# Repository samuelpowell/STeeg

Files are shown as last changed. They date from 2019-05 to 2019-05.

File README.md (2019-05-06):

# STeeg

# Startup
  - tPOR = 2^18 x tclk
  - tRST = 2 x tclk

# Form factor

 - To fit Takachi HEN110512 (S/B) external W111.2 x H54.7 x D120mm, internal 99.2W x H49.7 x D116mm.

# Configuration

  - Referential montage using SRB1 internally routed negative inputs.
  - Internal BIAS amplifier is used to reject interference and set patien common mode, components are chosen in bias amplifier feedback path to attain sufficient bandiwdth.
  - RC network on input is a low pass filter with differential capacitor to VREF, assuming fclk = 2.048MHz, the first alias is at fMOD = 1.024MHz and this should have good attenuation.

# Layout, power and passives.

  - AVDD and AVDD1 must be quiet. AVDD1 is the charge pump supply which may have switch transients. AVDD1 and AVSS1 should be starred, and each supply should be bypassed with 10u and 0.1u solid ceramic capacitors.
  - VCAP1 can be MLCC but for improved performance under vibration a tantalum or class 1 (C0G/NPO) should be used.
  - At output, provide VREF and VBIAS for differential capacitance and bias bpins
  - Decoupling capacitors and VCAP1 - VCAP4 should be as close as possible.
  - Optionally split analogue and digital planes, route over the appropriate plane
  - Use COG for differentials
  - 

# Architecture
 - 6-XV quiet input, isolated
 - 
# Component choices

 - Analogue LDO (TPS717 selected)
  - EVM uses TPS73225 on bipolar, 30uV (10-100kHz), 1% accuracy, 37dB @ 10kHz, 58dB @ 100Hz
  - TPS793 200mA, 70dB @ 10kHz, 112mv dropout, SOT-23
  - TPS77350, 55dB @ 1kHz, 30uV
  - TPS717XX, 70dB @ 1kHz, 67dB @100kHz, 30uV (100Hz - 100kHz), SOT-23

# Chaining multiple channels

# Notes

  - ADD LEDs
  - ADD Test Points
 - MICROCONTROLLER BOOT
 - MCU PROG
 - optional 3.3v external

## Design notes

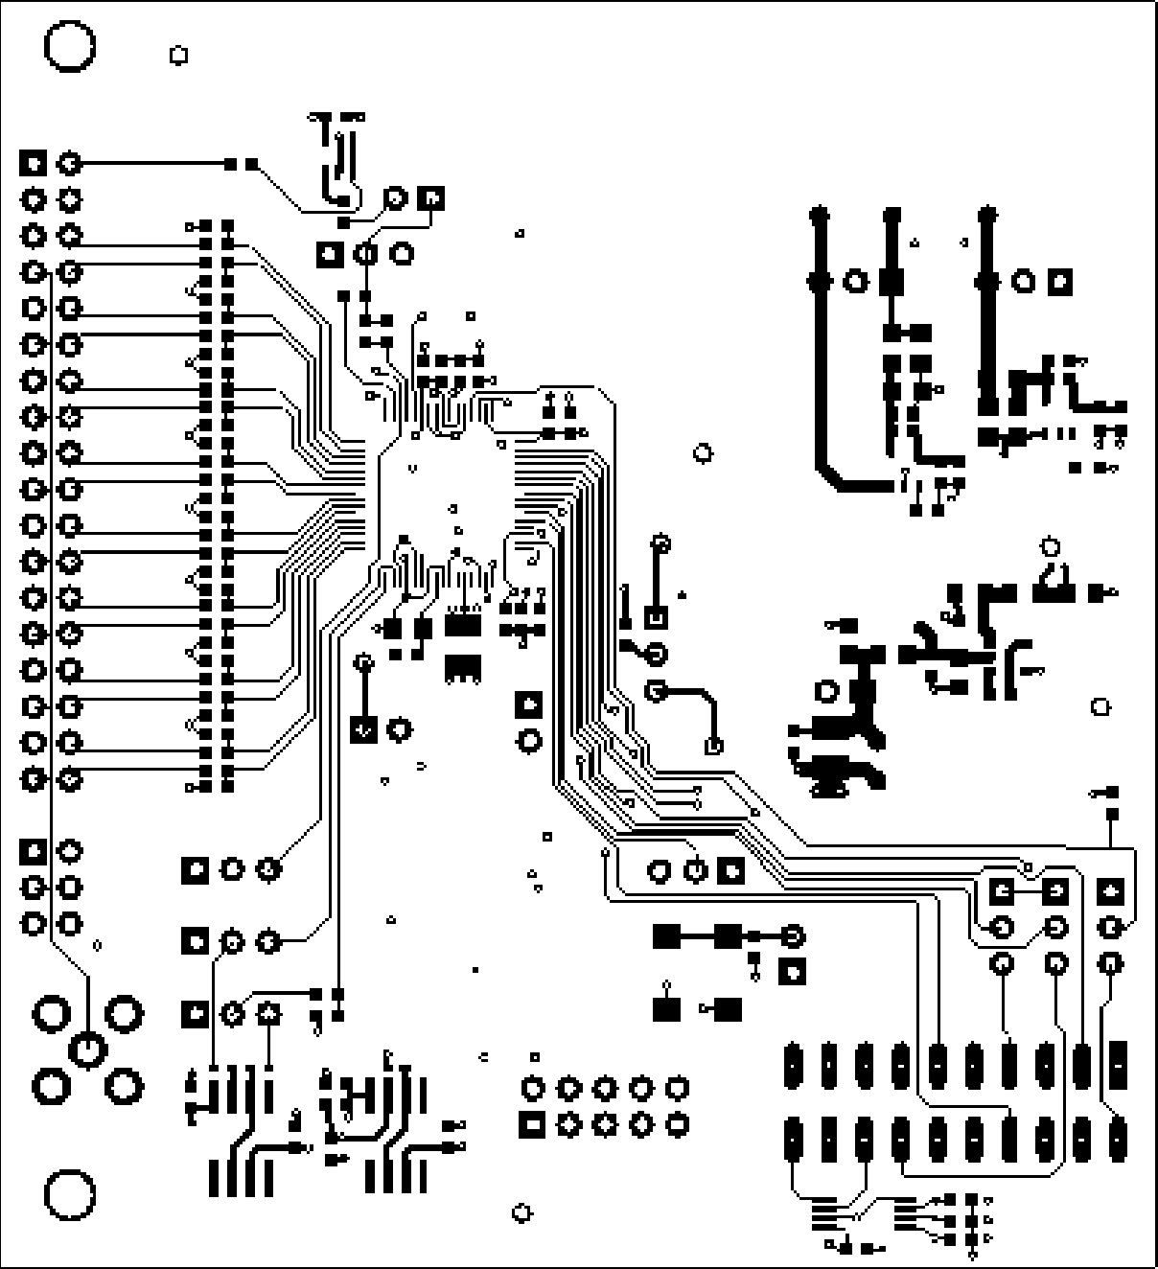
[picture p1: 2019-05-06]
evm_top.png

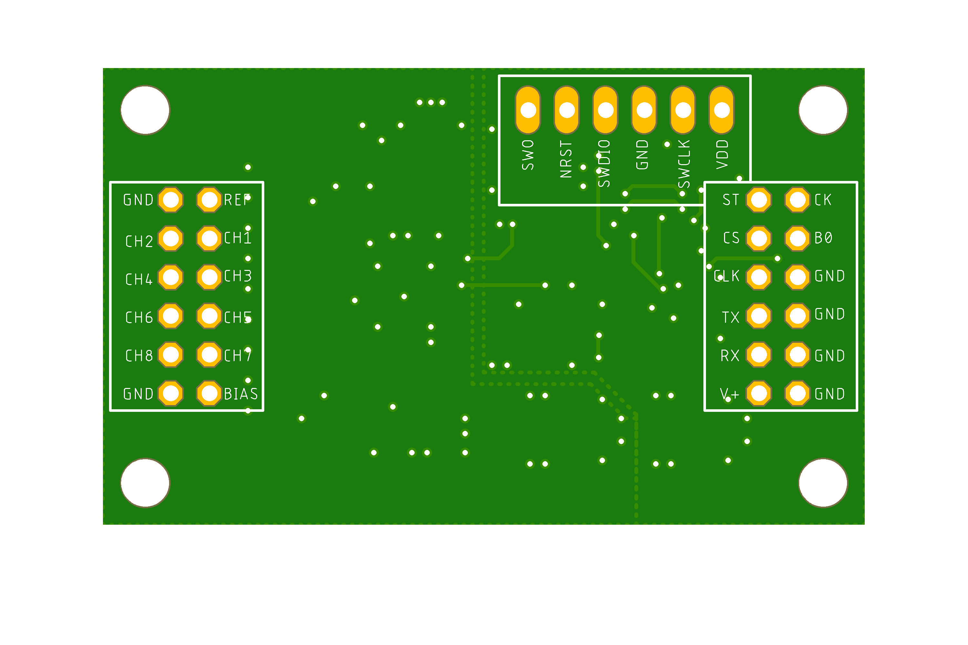
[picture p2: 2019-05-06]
stEEG/REV_A/stEEG_bottom.png

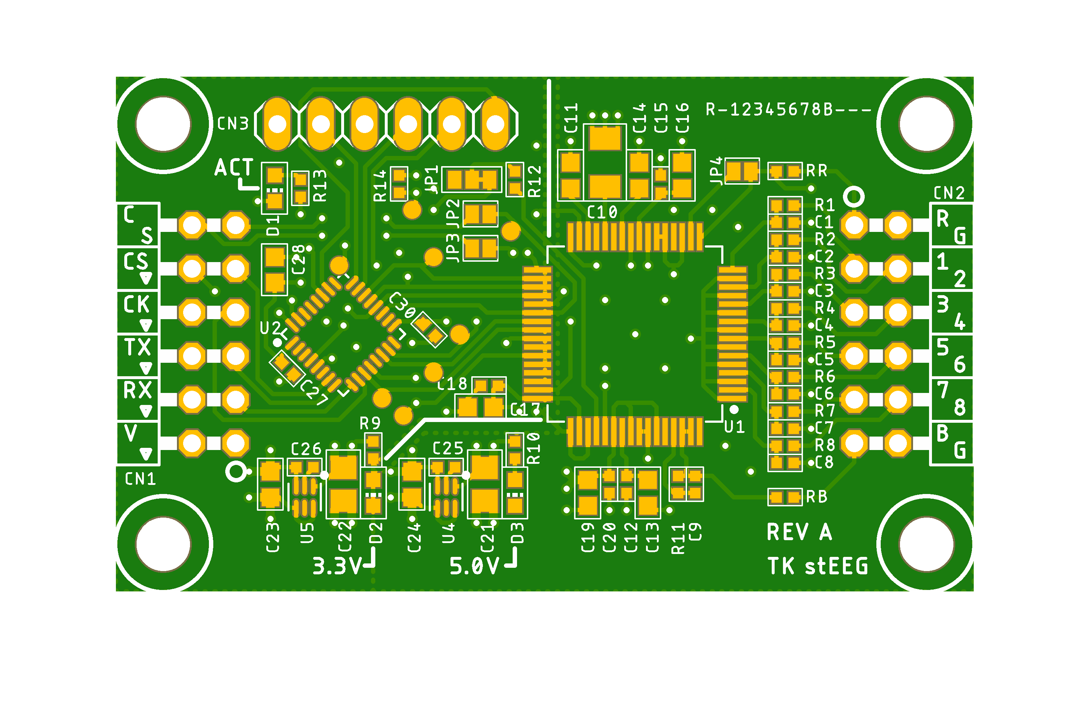
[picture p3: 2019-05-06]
stEEG/REV_A/stEEG_top.png

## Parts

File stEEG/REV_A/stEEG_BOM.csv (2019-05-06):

Parts | Qty | Value | Tolerance | Manufacturer | Part No | Digikiey | Package | Description
D1, D2, D3 | 3 |  |  | OSRAM Opto Semiconductors Inc. | LB Q39G-L2OO-35-1 | 475-2816-6-ND | 0603 | LED
CN3 | 1 |  |  | Molex | 901200126 | WM8076-ND |  | Pin header straight
CN1, CN2 | 2 |  |  | Molex | 10-88-3121 | WM23740-ND |  | Pin header 90 deg
R12, R14 | 2 | 100k | 1%, 0.0625W, 50V, 400ppm | Generic |  |  | 0402 | Resistor
C13, C15, C18, C20, C27, C30 | 6 | 100n | 10%, X7R, 16V | Generic |  |  | 0402 | Capacitor
C10 | 1 | 100u | 10%, X5R, 6.3V | Murata | GRM31CR60J107KE39L | 490-13982-1-ND | 1206 | Capacitor
C16, C28 | 2 | 10u | 10%, X5R, 16V | Murata | GRM188R61C106KAALD | 490-10728-1-ND | 0603 | Capacitor
C21, C22 | 2 | 10u | 10%, X7S, 16V | Murata | GRM21BC71C106KE11L | 490-12756-1-ND | 0805 | Capacitor
R9, R13 | 2 | 150R | 1%, 0.0625W, 50V, 400ppm | Generic |  |  | 0402 | Resistor
R11 | 1 | 1M | 1%, 0.0625W, 50V, 400ppm | Generic |  |  | 0402 | Resistor
R10 | 1 | 1k | 1%, 0.0625W, 50V, 400ppm | Generic |  |  | 0402 | Resistor
C9 | 1 | 1n5 | 10%, X7R, 50V | Generic |  |  | 0402 | Capacitor
C11, C12, C14, C17, C19, C23, C24 | 7 | 1u | 10%, X7R, 16V | Generic |  |  | 0603 | Capacitor
C25, C26 | 2 | 22n | 10%, X7R, 50V | Generic |  |  | 0402 | Capacitor
R1, R2, R3, R4, R5, R6, R7, R8, RB, RR | 10 | 4k99 | 1%, 0.0625W, 50V, 400ppm | Generic |  |  | 0402 | Resistor
C1, C2, C3, C4, C5, C6, C7, C8 | 8 | 4n7 | 10%, X7R, 50V | Generic |  |  | 0402 | Capacitor
U1 | 1 |  |  | Texas Instruments | ADS1299IPAG | 296-35009-ND | TQFP64 | 8-Channel, 24-Bit Analog-To-Digital Converter With Integrated EEG Front End
U2 | 1 |  |  | ST Microelectronics | STM32L432KCU3 | 497-18596-ND | QFN32 | Low-power ARM M4 microcontroller
U5 | 1 |  |  | Texas Instruments | TPS71733DSE | 296-32543-1-ND | SON8 | Low-Noise, High-Bandwidth PSRR, Low-Dropout, 150-mA Linear Regulator
U4 | 1 |  |  | Texas Instruments | TPS71750DSE | 296-25447-1-ND | SON8 | Low-Noise, High-Bandwidth PSRR, Low-Dropout, 150-mA Linear Regulator

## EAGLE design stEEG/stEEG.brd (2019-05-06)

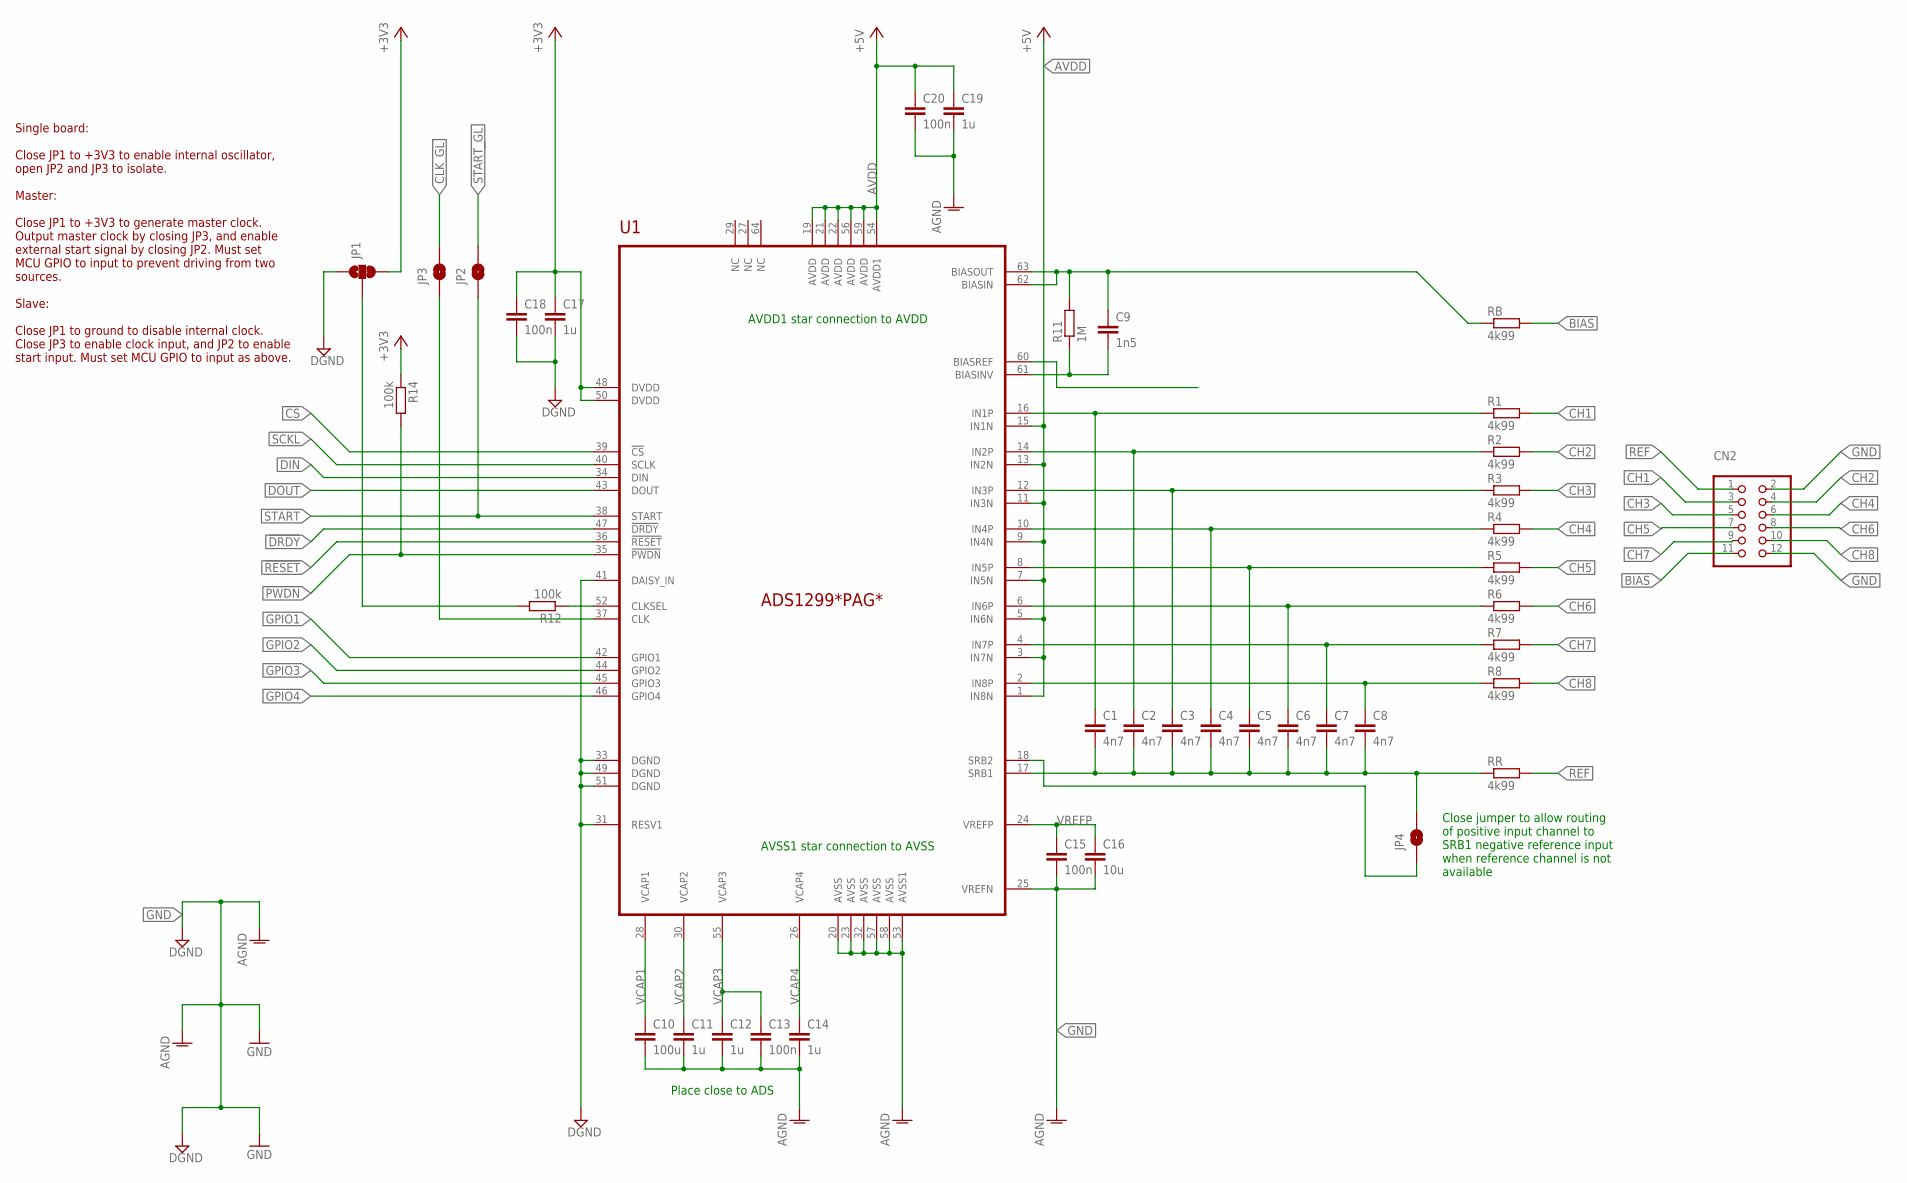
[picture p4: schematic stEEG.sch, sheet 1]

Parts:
C1, C2, C3, C4, C5, C6, C7, C8: 4n7; C0402
C9: 1n5; C0402
C10: 100u; C1206
C11, C12, C14, C17, C19: 1u; C0603
C13, C15, C18, C20: 100n; C0402
C16: 10u; C0603
CN2: PINHD-2X6/90; 2X06/90
JP1: JUMPER-SMT_3_1-NC_TRACE_SILK; SMT-JUMPER_3_1-NC_TRACE_SILK
JP2, JP3, JP4: JUMPER-SMT_2_NO_SILK; SMT-JUMPER_2_NO_SILK
R1, R2, R3, R4, R5, R6, R7, R8: 4k99; R0402
R11: 1M; R0402
R12, R14: 100k; R0402
RB: 4k99; R0402
RR: 4k99; R0402
U1: ADS1299*PAG*; PAG-PQFP64

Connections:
!CS: U1.39 (!CS); also elsewhere on the board
!DRDY: U1.47 (!DRDY); also elsewhere on the board
!PWDN: R14.2, U1.35 (!PWDN); also elsewhere on the board
!RESET: U1.36 (!RESET); also elsewhere on the board
+3V3: C17.1, C18.1, JP1.3, R14.1, U1.48 (DVDD), U1.50 (DVDD); also elsewhere on the board
AVDD: C19.1, C20.1, U1.1 (IN8N), U1.3 (IN7N), U1.5 (IN6N), U1.7 (IN5N), U1.9 (IN4N), U1.11 (IN3N), U1.13 (IN2N), U1.15 (IN1N), U1.19 (AVDD), U1.21 (AVDD), U1.22 (AVDD), U1.54 (AVDD1), U1.56 (AVDD), U1.59 (AVDD); also elsewhere on the board
BIAS: CN2.11, RB.2
CH1: CN2.3, R1.2
CH2: CN2.4, R2.2
CH3: CN2.5, R3.2
CH4: CN2.6, R4.2
CH5: CN2.7, R5.2
CH6: CN2.8, R6.2
CH7: CN2.9, R7.2
CH8: CN2.10, R8.2
CLK_GL: JP3.2; also elsewhere on the board
DIN: U1.34 (DIN); also elsewhere on the board
DOUT: U1.43 (DOUT); also elsewhere on the board
GND: C10.2, C11.2, C12.2, C13.2, C14.2, C15.2, C16.2, C17.2, C18.2, C19.2, C20.2, CN2.2, CN2.12, JP1.1, U1.20 (AVSS), U1.23 (AVSS), U1.25 (VREFN), U1.31 (RESV1), U1.32 (AVSS), U1.33 (DGND), U1.41 (DAISY_IN), U1.49 (DGND), U1.51 (DGND), U1.53 (AVSS1), U1.57 (AVSS), U1.58 (AVSS); also elsewhere on the board
GPIO1: U1.42 (GPIO1)
GPIO2: U1.44 (GPIO2)
GPIO3: U1.45 (GPIO3)
GPIO4: U1.46 (GPIO4)
unnamed: C1.1, R1.1, U1.16 (IN1P)
unnamed: R12.1, U1.52 (CLKSEL)
unnamed: C3.1, R3.1, U1.12 (IN3P)
unnamed: C4.1, R4.1, U1.10 (IN4P)
unnamed: C9.2, R11.1, U1.61 (BIASINV)
unnamed: C6.1, R6.1, U1.6 (IN6P)
unnamed: C7.1, R7.1, U1.4 (IN7P)
unnamed: C9.1, R11.2, RB.1, U1.62 (BIASIN), U1.63 (BIASOUT)
unnamed: C2.1, R2.1, U1.14 (IN2P)
unnamed: C5.1, R5.1, U1.8 (IN5P)
unnamed: C8.1, R8.1, U1.2 (IN8P)
unnamed: JP4.1, U1.18 (SRB2)
unnamed: JP1.2, R12.2
unnamed: JP3.1, U1.37 (CLK)
REF: CN2.1, RR.2
SCKL: U1.40 (SCLK); also elsewhere on the board
START: JP2.1, U1.38 (START); also elsewhere on the board
START_GL: JP2.2; also elsewhere on the board
VCAP1: C10.1, U1.28 (VCAP1)
VCAP2: C11.1, U1.30 (VCAP2)
VCAP3: C12.1, C13.1, U1.55 (VCAP3)
VCAP4: C14.1, U1.26 (VCAP4)
VREFP: C15.1, C16.1, U1.24 (VREFP)
VREFX: C1.2, C2.2, C3.2, C4.2, C5.2, C6.2, C7.2, C8.2, JP4.2, RR.1, U1.17 (SRB1)

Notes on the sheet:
AVDD1 star connection to AVDD
AVSS1 star connection to AVSS
Place close to ADS
Close jumper to allow routing of positive input channel to SRB1 negative reference input when reference channel is not available
Single board: Close JP1 to +3V3 to enable internal oscillator, open JP2 and JP3 to isolate. Master: Close JP1 to +3V3 to generate master clock. Output master clock by closing JP3, and enable external start signal by closing JP2. Must set MCU GPIO to input to prevent driving from two sources. Slave: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

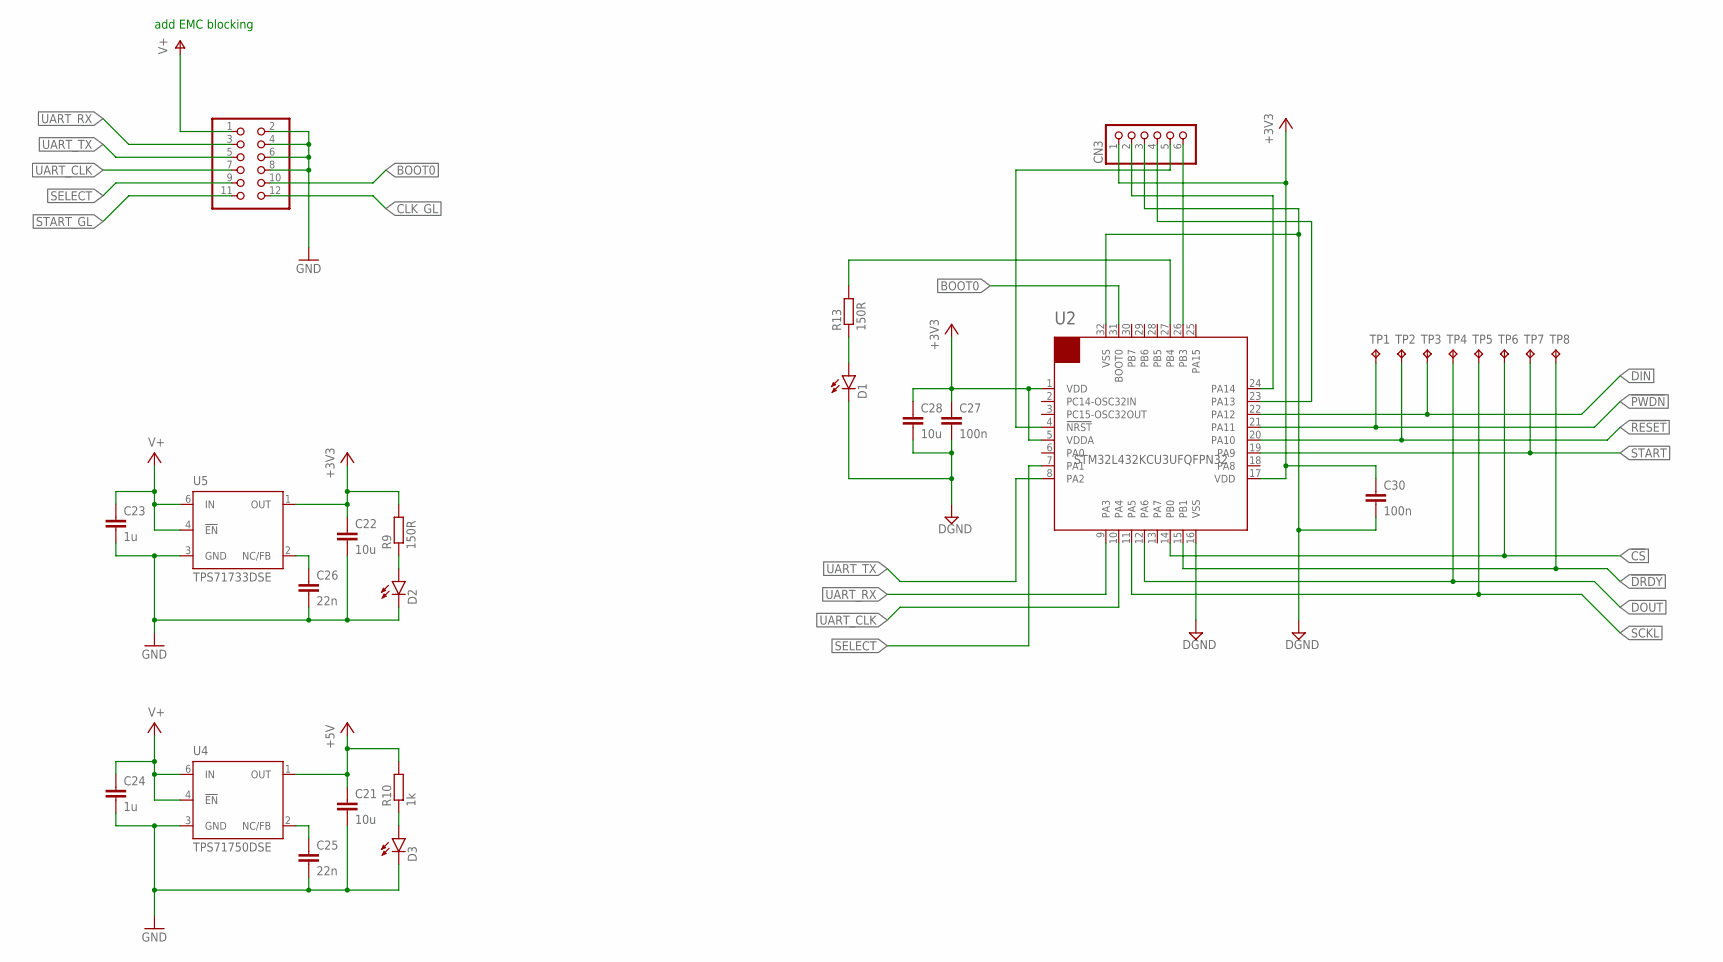
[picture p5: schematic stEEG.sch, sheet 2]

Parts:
C21, C22: 10u; C0805
C23, C24: 1u; C0603
C25, C26: 22n; C0402
C27, C30: 100n; C0402
C28: 10u; C0603
CN1: PINHD-2X6/90; 2X06/90
CN3: PINHD-1X6; 1X06
D1, D2, D3: LED0603; CHIP-LED0603
R9, R13: 150R; R0402
R10: 1k; R0402
TP1, TP2, TP3, TP4, TP5, TP6, TP7, TP8: TPTP10R; TP10R
U2: STM32L432KCU3UFQFPN32; QFN50P500X500X60-32
U4: TPS71750DSE; WSON-DSE
U5: TPS71733DSE; WSON-DSE

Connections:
!CS: TP6.TP, U2.14 (PB0); also elsewhere on the board
!DRDY: TP8.TP, U2.15 (PB1); also elsewhere on the board
!PWDN: TP1.TP, U2.21 (PA11); also elsewhere on the board
!RESET: TP2.TP, U2.20 (PA10); also elsewhere on the board
+3V3: C22.1, C27.1, C28.1, C30.1, CN3.1, R9.2, U2.1 (VDD), U2.5 (VDDA), U2.17 (VDD), U5.1 (OUT); also elsewhere on the board
AVDD: C21.1, R10.2, U4.1 (OUT); also elsewhere on the board
BOOT0: CN1.10, U2.31 (BOOT0)
CLK_GL: CN1.12; also elsewhere on the board
DIN: TP3.TP, U2.22 (PA12); also elsewhere on the board
DOUT: TP4.TP, U2.12 (PA6); also elsewhere on the board
GND: C21.2, C22.2, C23.2, C24.2, C25.2, C26.2, C27.2, C28.2, C30.2, CN1.2, CN1.4, CN1.6, CN1.8, CN3.3, D1.C, D2.C, D3.C, U2.16 (VSS), U2.32 (VSS), U4.3 (GND), U5.3 (GND); also elsewhere on the board
unnamed: D1.A, R13.1
unnamed: CN3.4, U2.23 (PA13)
unnamed: C26.1, U5.2 (NC/FB)
unnamed: CN3.2, U2.24 (PA14)
unnamed: CN3.6, U2.26 (PB3)
unnamed: CN3.5, U2.4 (!NRST)
unnamed: D2.A, R9.1
unnamed: R13.2, U2.27 (PB4)
unnamed: D3.A, R10.1
unnamed: C25.1, U4.2 (NC/FB)
SCKL: TP5.TP, U2.11 (PA5); also elsewhere on the board
SELECT: CN1.9, U2.7 (PA1)
START: TP7.TP, U2.19 (PA9); also elsewhere on the board
START_GL: CN1.11; also elsewhere on the board
UART_CLK: CN1.7, U2.10 (PA4)
UART_RX: CN1.3, U2.9 (PA3)
UART_TX: CN1.5, U2.8 (PA2)
V+: C23.1, C24.1, CN1.1, U4.4 (!EN), U4.6 (IN), U5.4 (!EN), U5.6 (IN)

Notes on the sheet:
add EMC blocking

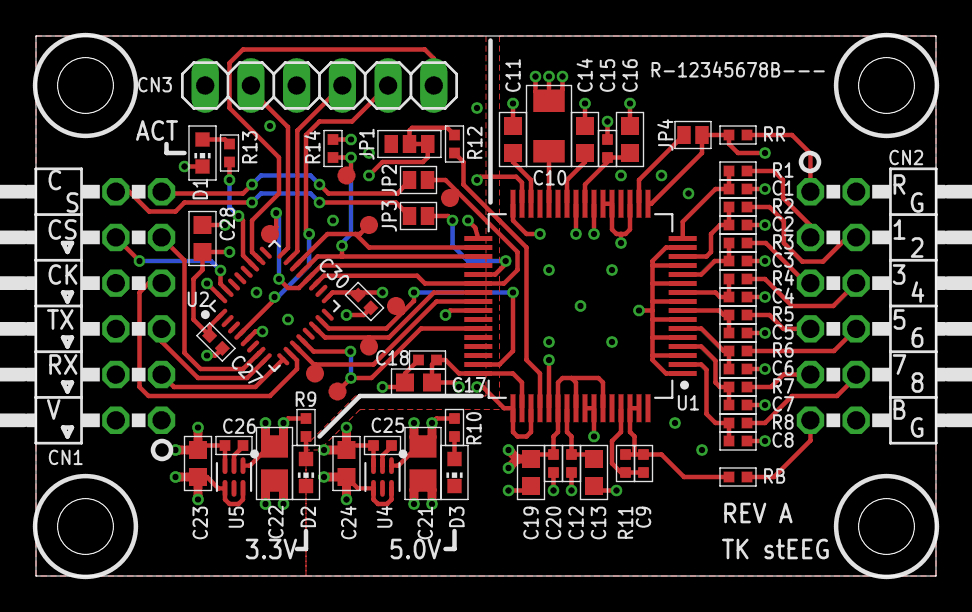
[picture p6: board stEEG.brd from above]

Board: 4 copper layers, 50.0 x 30.0 mm, 67 parts (0 on the bottom side), 59 nets.

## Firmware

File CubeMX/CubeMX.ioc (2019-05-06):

#MicroXplorer Configuration settings - do not modify
File.Version=6
KeepUserPlacement=false
Mcu.Family=STM32L4
Mcu.IP0=NVIC
Mcu.IP1=RCC
Mcu.IP2=SPI1
Mcu.IP3=SYS
Mcu.IP4=USART1
Mcu.IP5=USART2
Mcu.IPNb=6
Mcu.Name=STM32L432K(B-C)Ux
Mcu.Package=UFQFPN32
Mcu.Pin0=PA1
Mcu.Pin1=PA2
Mcu.Pin10=PA11
Mcu.Pin11=PA12
Mcu.Pin12=PA13 (JTMS-SWDIO)
Mcu.Pin13=PA14 (JTCK-SWCLK)
Mcu.Pin14=PB3 (JTDO-TRACESWO)
Mcu.Pin15=PB4 (NJTRST)
Mcu.Pin16=PB6
Mcu.Pin17=PB7
Mcu.Pin18=PH3-BOOT0
Mcu.Pin19=VP_SYS_VS_Systick
Mcu.Pin2=PA3
Mcu.Pin3=PA4
Mcu.Pin4=PA5
Mcu.Pin5=PA6
Mcu.Pin6=PB0
Mcu.Pin7=PB1
Mcu.Pin8=PA9
Mcu.Pin9=PA10
Mcu.PinsNb=20
Mcu.ThirdPartyNb=0
Mcu.UserConstants=
Mcu.UserName=STM32L432KCUx
MxCube.Version=5.2.0
MxDb.Version=DB.5.0.20
NVIC.BusFault_IRQn=true\:0\:0\:false\:false\:true\:false\:false
NVIC.DebugMonitor_IRQn=true\:0\:0\:false\:false\:true\:false\:false
NVIC.HardFault_IRQn=true\:0\:0\:false\:false\:true\:false\:false
NVIC.MemoryManagement_IRQn=true\:0\:0\:false\:false\:true\:false\:false
NVIC.NonMaskableInt_IRQn=true\:0\:0\:false\:false\:true\:false\:false
NVIC.PendSV_IRQn=true\:0\:0\:false\:false\:true\:false\:false
NVIC.PriorityGroup=NVIC_PRIORITYGROUP_4
NVIC.SVCall_IRQn=true\:0\:0\:false\:false\:true\:false\:false
NVIC.SysTick_IRQn=true\:0\:0\:false\:false\:true\:false\:true
NVIC.UsageFault_IRQn=true\:0\:0\:false\:false\:true\:false\:false
PA1.GPIOParameters=GPIO_Label
PA1.GPIO_Label=SELECT
PA1.Locked=true
PA1.Signal=GPIO_Input
PA10.GPIOParameters=GPIO_Label
PA10.GPIO_Label=NRST
PA10.Locked=true
PA10.Signal=GPIO_Output
PA11.GPIOParameters=GPIO_Label
PA11.GPIO_Label=NPWDN
PA11.Locked=true
PA11.Signal=GPIO_Output
PA12.Locked=true
PA12.Mode=Full_Duplex_Master
PA12.Signal=SPI1_MOSI
PA13\ (JTMS-SWDIO).Mode=Trace_Asynchronous_SW
PA13\ (JTMS-SWDIO).Signal=SYS_JTMS-SWDIO
PA14\ (JTCK-SWCLK).Mode=Trace_Asynchronous_SW
PA14\ (JTCK-SWCLK).Signal=SYS_JTCK-SWCLK
PA2.Mode=Synchronous
PA2.Signal=USART2_TX
PA3.Mode=Synchronous
PA3.Signal=USART2_RX
PA4.Mode=Synchronous
PA4.Signal=USART2_CK
PA5.Mode=Full_Duplex_Master
PA5.Signal=SPI1_SCK
PA6.Mode=Full_Duplex_Master
PA6.Signal=SPI1_MISO
PA9.GPIOParameters=GPIO_Label
PA9.GPIO_Label=START
PA9.Locked=true
PA9.Signal=GPIO_Output
PB0.Locked=true
PB0.Mode=NSS_Signal_Hard_Output
PB0.Signal=SPI1_NSS
PB1.GPIOParameters=GPIO_Label
PB1.GPIO_Label=NDRDY
PB1.Locked=true
PB1.Signal=GPIO_Input
PB3\ (JTDO-TRACESWO).Mode=Trace_Asynchronous_SW
PB3\ (JTDO-TRACESWO).Signal=SYS_JTDO-SWO
PB4\ (NJTRST).GPIOParameters=GPIO_Label
PB4\ (NJTRST).GPIO_Label=LED_ACT
PB4\ (NJTRST).Locked=true
PB4\ (NJTRST).Signal=GPIO_Output
PB6.Mode=Half_duplex(single_wire_mode)
PB6.Signal=USART1_TX
PB7.Mode=Mode_PVD_Ext
PB7.Signal=SYS_PVD_IN
PCC.Checker=true
PCC.Line=STM32L4x2
PCC.MCU=STM32L432K(B-C)Ux
PCC.PartNumber=STM32L432KCUx
PCC.Seq0=0
PCC.Series=STM32L4
PCC.Temperature=25
PCC.Vdd=3.0
PH3-BOOT0.GPIOParameters=GPIO_Label
PH3-BOOT0.GPIO_Label=BOOT0
PH3-BOOT0.Locked=true
PH3-BOOT0.Signal=GPIO_Input
PinOutPanel.RotationAngle=0
ProjectManager.AskForMigrate=true
ProjectManager.BackupPrevious=false
ProjectManager.CompilerOptimize=6
ProjectManager.ComputerToolchain=false
ProjectManager.CoupleFile=false
ProjectManager.CustomerFirmwarePackage=
ProjectManager.DefaultFWLocation=true
ProjectManager.DeletePrevious=true
ProjectManager.DeviceId=STM32L432KCUx
ProjectManager.FirmwarePackage=STM32Cube FW_L4 V1.14.0
ProjectManager.FreePins=false
ProjectManager.HalAssertFull=false
ProjectManager.HeapSize=0x200
ProjectManager.KeepUserCode=true
ProjectManager.LastFirmware=true
ProjectManager.LibraryCopy=0
ProjectManager.MainLocation=Src
ProjectManager.NoMain=false
ProjectManager.PreviousToolchain=
ProjectManager.ProjectBuild=false
ProjectManager.ProjectFileName=CubeMX.ioc
ProjectManager.ProjectName=CubeMX
ProjectManager.StackSize=0x400
ProjectManager.TargetToolchain=EWARM V8
ProjectManager.ToolChainLocation=
ProjectManager.UnderRoot=false
ProjectManager.functionlistsort=
RCC.ADCFreq_Value=64000000
RCC.AHBFreq_Value=80000000
RCC.APB1Freq_Value=80000000
RCC.APB1TimFreq_Value=80000000
RCC.APB2Freq_Value=80000000
RCC.APB2TimFreq_Value=80000000
RCC.CortexFreq_Value=80000000
RCC.FCLKCortexFreq_Value=80000000
RCC.FamilyName=M
RCC.HCLKFreq_Value=80000000
RCC.HSE_VALUE=8000000
RCC.HSI48_VALUE=48000000
RCC.HSI_VALUE=16000000
RCC.I2C1Freq_Value=80000000
RCC.I2C3Freq_Value=80000000
RCC.IPParameters=ADCFreq_Value,AHBFreq_Value,APB1Freq_Value,APB1TimFreq_Value,APB2Freq_Value,APB2TimFreq_Value,CortexFreq_Value,FCLKCortexFreq_Value,FamilyName,HCLKFreq_Value,HSE_VALUE,HSI48_VALUE,HSI_VALUE,I2C1Freq_Value,I2C3Freq_Value,LPTIM1Freq_Value,LPTIM2Freq_Value,LPUART1Freq_Value,LSCOPinFreq_Value,LSE_VALUE,LSI_VALUE,MCO1PinFreq_Value,MSI_VALUE,PLLN,PLLPoutputFreq_Value,PLLQoutputFreq_Value,PLLR,PLLRCLKFreq_Value,PLLSAI1PoutputFreq_Value,PLLSAI1QoutputFreq_Value,PLLSAI1RoutputFreq_Value,PLLSourceVirtual,PWRFreq_Value,RNGFreq_Value,SAI1Freq_Value,SWPMI1Freq_Value,SYSCLKFreq_VALUE,SYSCLKSource,USART1Freq_Value,USART2Freq_Value,USBFreq_Value,VCOInputFreq_Value,VCOOutputFreq_Value,VCOSAI1OutputFreq_Value
RCC.LPTIM1Freq_Value=80000000
RCC.LPTIM2Freq_Value=80000000
RCC.LPUART1Freq_Value=80000000
RCC.LSCOPinFreq_Value=32000
RCC.LSE_VALUE=32768
RCC.LSI_VALUE=32000
RCC.MCO1PinFreq_Value=80000000
RCC.MSI_VALUE=4000000
RCC.PLLN=20
RCC.PLLPoutputFreq_Value=45714285.71428572
RCC.PLLQoutputFreq_Value=160000000
RCC.PLLR=RCC_PLLR_DIV4
RCC.PLLRCLKFreq_Value=80000000
RCC.PLLSAI1PoutputFreq_Value=18285714.285714287
RCC.PLLSAI1QoutputFreq_Value=64000000
RCC.PLLSAI1RoutputFreq_Value=64000000
RCC.PLLSourceVirtual=RCC_PLLSOURCE_HSI
RCC.PWRFreq_Value=80000000
RCC.RNGFreq_Value=64000000
RCC.SAI1Freq_Value=18285714.285714287
RCC.SWPMI1Freq_Value=80000000
RCC.SYSCLKFreq_VALUE=80000000
RCC.SYSCLKSource=RCC_SYSCLKSOURCE_PLLCLK
RCC.USART1Freq_Value=80000000
RCC.USART2Freq_Value=80000000
RCC.USBFreq_Value=64000000
RCC.VCOInputFreq_Value=16000000
RCC.VCOOutputFreq_Value=320000000
RCC.VCOSAI1OutputFreq_Value=128000000
SPI1.CalculateBaudRate=40.0 MBits/s
SPI1.Direction=SPI_DIRECTION_2LINES
SPI1.IPParameters=VirtualType,Mode,Direction,CalculateBaudRate,VirtualNSS
SPI1.Mode=SPI_MODE_MASTER
SPI1.VirtualNSS=VM_NSSHARD
SPI1.VirtualType=VM_MASTER
USART1.IPParameters=VirtualMode-Half_duplex(single_wire_mode)
USART1.VirtualMode-Half_duplex(single_wire_mode)=VM_ASYNC
USART2.BaudRate=4800000
USART2.IPParameters=VirtualMode-Synchronous,BaudRate
USART2.VirtualMode-Synchronous=VM_SYNC
VP_SYS_VS_Systick.Mode=SysTick
VP_SYS_VS_Systick.Signal=SYS_VS_Systick
board=custom

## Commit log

2019-05-06 Initial design, pass ERC, DRC
    [stEEG.brd, stEEG.sch]
2019-05-06 Tweak silk, add CAM, generate REV_A mfg
    [copper_bottom_l4.gbr, copper_inner_l2.gbr, copper_inner_l3.gbr, copper_top_l1.gbr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]
2019-05-06 Save ater RevA
    [stEEG.brd]
